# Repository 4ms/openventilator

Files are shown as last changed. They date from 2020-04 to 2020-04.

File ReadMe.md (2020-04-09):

# OpenVentilator

This project is a collaboration to update the OpenVentilator files provided by Medtronic to modern KiCad format as well as update BoM to currently available components.

If you'd like to contribute, please contact Seth (seth@kipro-pcb.com) for details.

## Getting Started

This includes links to useful resources and defines prerequisite programs or tools for contributing.

### SSH Keys

It is recommended to use a [SSH key](https://docs.gitlab.com/ee/gitlab-basics/create-your-ssh-keys.html) to pull/push.

For Windows users, [follow these instructions](https://docs.joyent.com/public-cloud/getting-started/ssh-keys/generating-an-ssh-key-manually/manually-generating-your-ssh-key-in-windows) to create an SSH key.

### Useful Resources

[Google Drive](https://drive.google.com/drive/folders/1fBbcaIb6aupdgDmfqB_Z8kfAjUOgFtCi) - Project specific Google drive.

[Medtronic Releases](https://www.medtronic.com/us-en/e/open-files/thank-you.html)

[GitLab basics guides](https://docs.gitlab.com/ee/gitlab-basics/)

[Gitflow](https://datasift.github.io/gitflow/IntroducingGitFlow.html)

### Tools

Install [Git](https://git-scm.com/) on your computer.

Either use KiCAD version 5.1.5 or the nightly builds.

[KiCAD v5.1.5](https://kicad-pcb.org/download/) - preferred

[KiCAD Nigthly Builds](https://launchpad.net/~js-reynaud/+archive/ubuntu/ppa-kicad)

**GerbView** - part of KiCAD.

File → Open Gerber Files. In “File Name” select *.phd for CR-5000 designs. Some of the polygons are not handled correctly in 5.1.5-3.

[PentaLogix ViewMate Free (Windows)](https://www.pentalogix.com/t/software-products/viewmate) 

You will need to create an account to download and get a serial number. Run File → Import → Gerber and then control-select all the .phd files for CR-5000 designs.

[GerberLogix](https://www.easylogix.de/products_detail.php?prog_id=1)

Works well with the free version for .phd files.  A little simpler than ViewMate

## Contributing

Please read [Contributing.md](Contributing.md) for information on cloning, branching, and sharing your work.

## Versioning

We should adhere to [SemVer](https://semver.org/) for our versioning process. Each PCB will have its own version number.

*Note that this is not completely settled.*

## Channels and Leads

If you are interested in working on a specific board, please head to the respective channels in the Slack organization. The leads for each board are provided below as well.

Be sure to check for pinned messages as well as the channel topic for more information as well.

### Hardware
**#battery-connection-board** for the Battery Connection Board. Lead by Valerie Hanson.

**#blower-driver-board** for the Blower Command Board. Lead by Gabe Soares.

**#buzzer-board** for the Buzzer Board RB0505. Lead by Yannick Liotta.

**#cpu-board** for the CPU Board. Lead by Seth Hillbrand.

**#mechanical-prototyping** for all mechanical components. Currently no lead.

**#power-management-board** for the Power Supply Board (Tantalum Less). Lead by Paul Petersen.

**#powerpack-board** for the Power Pack Board. Lead by George Ioakimedes.

**#turbine** for the blower turbine motor. Currently no lead.

### Firmware
**#firmware-pic** for questions relating to the PIC Firmware. Currently no lead.

**#firmware-st10** for questions relating to the ST Micro Firmware. Lead by Melvin Aguirre.

### Project Related
**#how-to-get-started** for help in setting up any part of the project. Lead by Adam Drewery.

**#general** for questions that you're unsure where they would belong.

**#openventilator** for high-level project discussions. For example, what version of KiCAD to use?

**#parts** for any questions related to parts. This can be creating them in KiCAD or sourcing them. For sourcing contact Ritika Sahai-Kar or Sophi Kravitz. For parts creation contact Adam Drewery.

## Parts

If creating new parts, follow the [KiCAD Library Convention](https://kicad-pcb.org/libraries/klc/).

Passives are an exception to this rule. Please create a library part per MPN.

### Symbol Parameters

The following fields are *required* for all parts.

**Reference**

**Value**

**Footprint**

**Documentation**

**Description**

**Item Number** - This is Medtronic's Item Number called out in their documentation.

**Manufacturer**

**Manufacturer_No**

### Pointing to the right libraries

Be sure you are not pointing to your own libraries. We want to work within the OpenVentilator project library.

Within a KiCAD project, click on Preferences -> Manage Symbol Libraries.

The Path to the libraries should contain **${KIPRJMOD}**.

*Note: The libraries are ultimately going to be brought into their own directory in the project. We will keep you posted with more information.*

## License

This project is licensed under the [Permissive License - Open Ventilator](Permissive License--Open Ventilator.pdf).

## Acknowledgements

Thanks to Marc Hillman for his contribution to the Battery Connection Board.

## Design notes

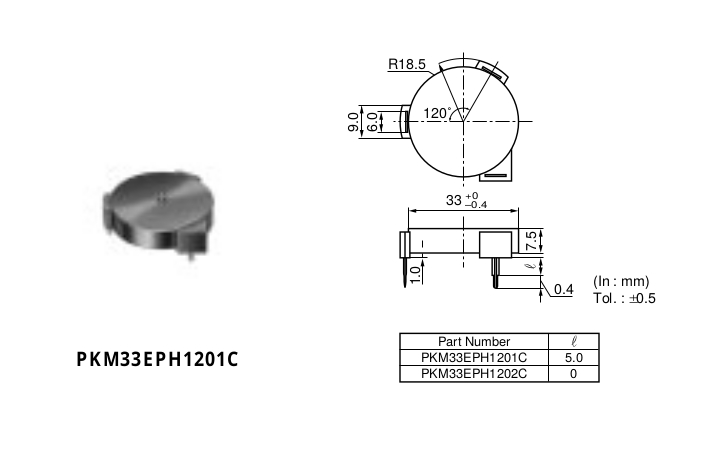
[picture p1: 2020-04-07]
GR106768 Buzzer/doc/PKM33EPH1201C.jpg

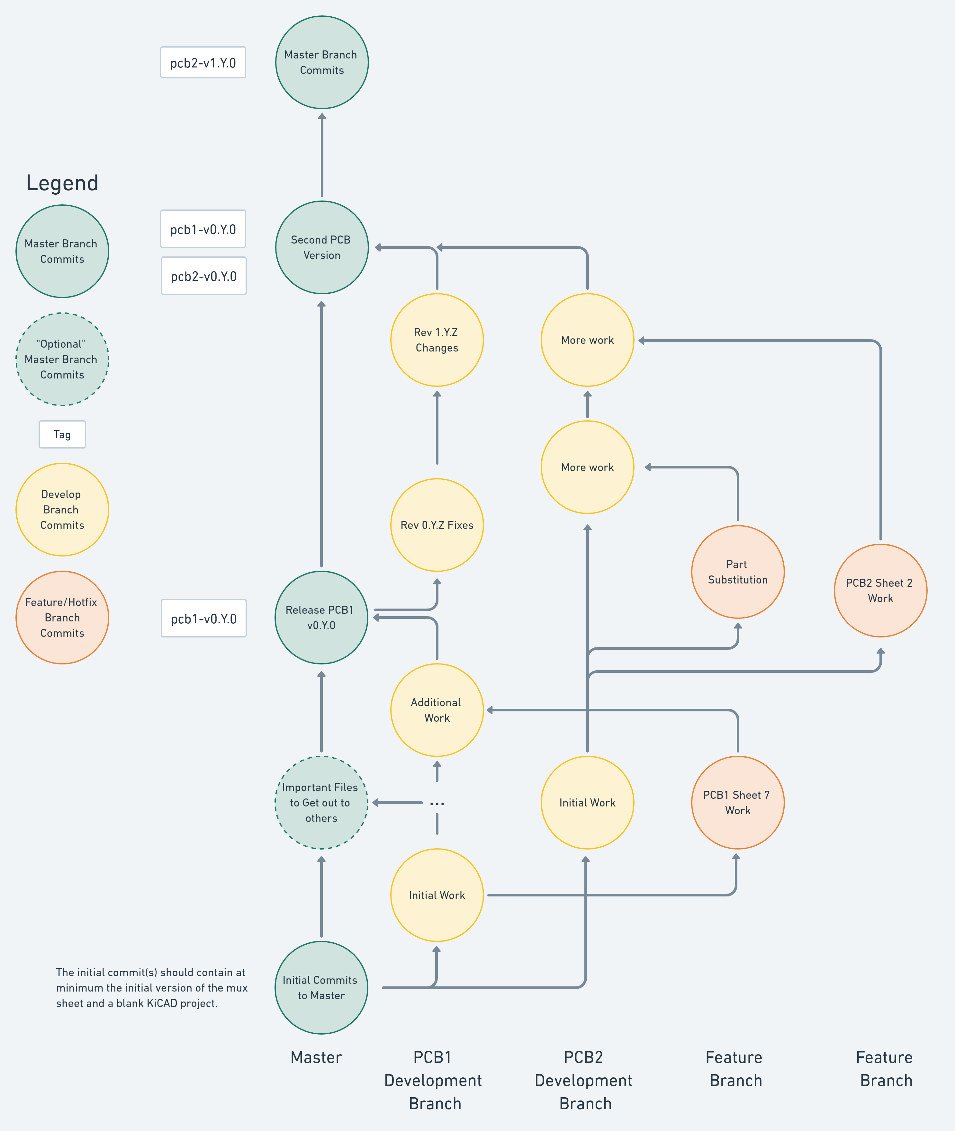
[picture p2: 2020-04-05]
git_version_control.png

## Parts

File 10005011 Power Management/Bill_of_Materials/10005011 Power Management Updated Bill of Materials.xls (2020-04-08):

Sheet: BoM Parts
Items in bold are left to do, awaiting info or just notes
Information current as of 4/7/2020
Item Description | Original Mfgr | Original Mfgr_PN | Qty | Ref Des | Mfgr | Mfgr_PN | Description | Source | Source_PN | Datasheet
POWER SUPPLY, 220VAC, 33VDC, 100W | XP POWER PLC | ECM100US33>2413 | 1 | ALIM1 | Note: Reached out to XP Power 4/3 inquiring about this part.
CAPACITOR,100NF,16V,+/-10%,X7R,0402 | MURATA | GRM155R71C104JA88J | 43 | C1,C3,C4,C5,C6,C8,C9,C12,C13,C15,C17,C25,C35,C36,C46,C58,C59,C63,C64,C69,C71,C75,C78,C82,C85,C86,C87,C88,C91,C92,C93,C96,C97,C101,C102,C103,C104,C105,C108,C122,C123,C124,C126 | Murata Electronics | GCM155R71C104KA55J | CAP CER 0.1UF 16V X7R 0402 | Digi-Key | 490-7998-1-ND | https://psearch.en.murata.com/capacitor/product/GCM155R71C104KA55%23.pdf
CAPACITOR CERAMIC, 10UF,+/-10%,50V | AVX | 22205C106K4Z4A | 19 | C10,C11,C14,C20,C26,C27,C28,C40,C41,C43,C51,C60,C66,C67,C73,C114,C136,C137,C138 | TDK Corporation | CGA9N3X7R1H106K230KB | CAP CER 10UF 50V X7R 2220 | Digi-Key | 445-7932-1-ND | https://product.tdk.com/info/en/catalog/datasheets/mlcc_automotive_general_en.pdf?ref_disty=digikey
CAPACITOR CERAMIC, 22UF,+/-10%,25V | KEMET_RMS1 | C2220X226K3RAC | 1 | C107 | KEMET | C2220X226K3RACAUTO | CAP CER 22UF 25V X7R 2220 | Digi-Key | 399-7061-1-ND | https://api.kemet.com/component-edge/download/specsheet/C2220X226K3RACAUTO.pdf
CAPACITOR,470PF,+/-10%,50V,0402 | VISHAY_RMS1 | VJ0402Y471KXAAC | 1 | C16 | Murata Electronics | GCM155R71H471KA37D | CAP CER 470PF 50V X7R 0402 | Digi-Key | 490-4913-1-ND | https://psearch.en.murata.com/capacitor/product/GCM155R71H471KA37%23.pdf
CAPACITOR CERAMIC,10NF,+/-10%,50V,0603 | YAGEO_RMS1 | 223858615636 | 15 | C18,C19,C22,C37,C47,C49,C52,C83,C99,C111,C115,C116,C117,C118,C119 | Yageo | CC0603KRX7R9BB103 | CAP CER 10000PF 50V X7R 0603 | Digi-Key | 311-1085-1-ND | https://www.yageo.com/upload/media/product/productsearch/datasheet/mlcc/UPY-GPHC_X7R_6.3V-to-50V_18.pdf
CAPACITOR CERAMIC, 10UF,+/-10%,16V | KEMET_RMS1 | C0805C106K4PAC | 2 | C2,C45 | KEMET | C0805C106K4PACTU | CAP CER 10UF 16V X5R 0805 | Digi-Key | 399-8012-1-ND | https://api.kemet.com/component-edge/download/datasheet/C0805C106K4PACTU.pdf
CAPACITOR CERAMIC, 4.7UF,+/-10%,50V | KEMET | C1210C475K5RACAUTO | 5 | C21,C29,C90,C134,C135 | KEMET | C1210C475K5RACAUTO | CAP CER 4.7UF 50V X7R 1210 | Digi-Key | 399-7049-1-ND | https://api.kemet.com/component-edge/download/specsheet/C1210C475K5RACAUTO.pdf
CAPACITOR CERAMIC, 100NF, +/-10%, 50V, X7R,0805 | YAGEO_RMS1 | 223858055649 | 15 | C23,C31,C55,C70,C79,C106,C109,C110,C112,C113,C131,C132,C133,C140,C141 | Yageo | CC0805KRX7R9BB104 | CAP CER 0.1UF 50V X7R 0805 | Digi-Key | 311-1140-1-ND | https://www.yageo.com/upload/media/product/productsearch/datasheet/mlcc/UPY-GPHC_X7R_6.3V-to-50V_18.pdf
CAPACITOR CERAMIC,4.7NF,+/-10%,50V,0603 | KEMET_RMS1 | C0603C472K5RACTU | 1 | C24 | KEMET | C0603C472K5RACTU | CAP CER 4700PF 50V X7R 0603 | Digi-Key | 399-1087-1-ND | https://api.kemet.com/component-edge/download/datasheet/C0603C472K5RACTU.pdf
CAPACITOR,4.7UF,+/-10%,16V, X5R, 0805 | AVX_RMS1 | 0805YD475KAT2A | 2 | C30,C80 | AVX Corporation | 0805YD475KAT2A | CAP CER 4.7UF 16V X5R 0805 | Digi-Key | 478-5166-1-ND | http://datasheets.avx.com/cx5r.pdf
CAPACITOR, 1UF, +/-10%, 16V, 0805 | AVX_RMS1 | 0805YC105KAT2A | 2 | C32,C57 | AVX Corporation | 0805YC105KAT2A | CAP CER 1UF 16V X7R 0805 | Digi-Key | 478-5034-1-ND | http://datasheets.avx.com/X7RDielectric.pdf
CAPACITOR,2.2UF,+/-10%,16V,1206 | MURATA MANUFACTURING CO., LTD. | GCM31MR71E225KA57L | 1 | C33 | Taiyo Yuden | EMK316B7225KLHT | CAP CER 2.2UF 16V X7R 1206 | Digi-Key | 587-3329-1-ND | https://ds.yuden.co.jp/TYCOMPAS/ut/detail?pn=EMK316B7225KLHT%20%20&u=M
CAPACITOR CERAMIC, 22UF,+/-10%,16V | JOHANSON DIELECTRICS_RMS1 | 160S41X226KV4E | 2 | C34,C65 | Taiyo Yuden | EMK325BJ226KMHP | CAP CER 22UF 16V X5R 1210 | Digi-Key | 587-5432-1-ND | https://ds.yuden.co.jp/TYCOMPAS/ut/detail?pn=EMK325BJ226KMHP%20&u=M
CAPACITOR,220NF,+/-20%,16V,0603 | VISHAY_RMS1 | VJ0603V224MXJCW1BC | 2 | C38,C39 | TDK Corporation | CGA3E2X7R1C224M080AA | CAP CER 0.22UF 16V X7R 0603 | Digi-Key | 445-12535-1-ND | https://product.tdk.com/info/en/catalog/datasheets/mlcc_automotive_general_en.pdf?ref_disty=digikey
CAPACITOR ELECTROLYTIC, 330UF,35V | PANASONIC_RMS1 | EEEFK1V331P | 2 | C42,C125 | Panasonic Electronic Components | EEE-FK1V331P | CAP ALUM 330UF 20% 35V SMD | Digi-Key | PCE3841CT-ND | http://industrial.panasonic.com/www-cgi/jvcr13pz.cgi?E+PZ+3+ABA0120+EEEFK1V331P+7+WW
CAPACITOR ELECTROLYTIC, 220UF,16V+/-20% | PANASONIC_RMS1 | EEEFK1C221P | 1 | C44 | Panasonic Electronic Components | EEE-FK1C221P | CAP ALUM 220UF 20% 16V SMD | Digi-Key | PCE3787CT-ND | http://industrial.panasonic.com/www-cgi/jvcr13pz.cgi?E+PZ+3+ABA0120+EEEFK1C221P+7+WW
CAPACITOR,47 PF,+/-5%,50V,0402 | MURATA MANUFACTURING CO., LTD. | GRM1555C1H470JA01D | 7 | C48,C120,C121,C127,C128,C129,C130 | Murata Electronics | GCM1555C1H470JA16D | CAP CER 47PF 50V C0G/NP0 0402 | Digi-Key | 490-10670-1-ND | https://www.murata.com/~/media/webrenewal/support/library/catalog/products/capacitor/mlcc/c03e.ashx?la=en-us
CAPACITOR,220NF,+/-10%,16V,X7R,1206 | VISHAY_RMS1 | VJ1206Y224JXAAT | 1 | C50 | KEMET | C1206C224J5RACTU | CAP CER 0.22UF 50V X7R 1206 | Digi-Key | 399-1252-1-ND | https://api.kemet.com/component-edge/download/datasheet/C1206C224J5RACTU.pdf
CAPACITOR ARRAY, 47PF, 50V, +/-10%,NPO,0612 | YAGEO_RMS1 | 225514611532 | 5 | C53,C61,C62,C98,C100 | KEMET | CA064C470K5GAC7800 | CAP ARRAY 47PF 50V NP0 0612 | Digi-Key | 399-10028-1-ND | https://media.digikey.com/pdf/Data%20Sheets/Kemet%20PDFs/COG_Dielectric_Rev_Mar_2015.pdf
CAPACITOR ELECTROLYTIC, 100UF,35V,+/-10% | PANASONIC_RMS1 | EEEFK1V101P | 1 | C54 | Panasonic Electronic Components | EEE-FK1V101P | CAP ALUM 100UF 20% 35V SMD | Digi-Key | PCE3835CT-ND | http://industrial.panasonic.com/www-cgi/jvcr13pz.cgi?E+PZ+3+ABA0120+EEEFK1V101P+7+WW
CAPACITOR,56PF,50V,+/-5%,0603,NPO | YAGEO_RMS1 | 223886715569 | 1 | C68 | Yageo | CC0603JRNPO9BN560 | CAP CER 56PF 50V C0G/NPO 0603 | Digi-Key | 311-1066-1-ND | https://www.yageo.com/upload/media/product/productsearch/datasheet/mlcc/UPY-GP_NP0_16V-to-50V_18.pdf
CAPACITOR, 33PF, +/-5%,50V,NPO, 0603 | MURATA MANUFACTURING CO., LTD. | GRM1885C1H330JA01D | 1 | C7 | Samsung Electro-Mechanics | CL10C330JB81PNC | CAP CER 33PF 50V C0G/NP0 0603 | Digi-Key | 1276-2264-1-ND | http://www.samsungsem.com/kr/support/product-search/mlcc/CL10C330JB81PNC.jsp
CAPACITOR,33NF,+/-10%,16V,X7R,0603 | AVX_RMS1 | 0603YC333KAT2A | 1 | C72 | AVX Corporation | 0603YC333KAT2A | CAP CER 0.033UF 16V X7R 0603 | Digi-Key | 478-5898-1-ND | http://datasheets.avx.com/X7RDielectric.pdf
CAPACITOR,1NF,+/-10%,50V,X7R,0603 | AVX_RMS1 | 06035C102KAT2A | 1 | C74 | AVX Corporation | 06035C102KAT2A | CAP CER 1000PF 50V X7R 0603 | Digi-Key | 478-1215-1-ND | http://datasheets.avx.com/X7RDielectric.pdf
CAPACITOR,330NF,+/-10%,16V,0805,X7R | YAGEO_RMS1 | 222278015556 | 1 | C76 | Yageo | CC0805JKX7R7BB334 | CAP CER 0.33UF 16V X7R 0805 | Digi-Key | 311-4215-1-ND | https://www.yageo.com/upload/media/product/productsearch/datasheet/mlcc/UPY-GPHC_X7R_6.3V-to-50V_18.pdf
CAPACITOR,100PF,50V,+/-5%,C0G,0402 | MURATA MANUFACTURING CO., LTD. | GRM1555C1H101JD01D | 2 | C77,C81 | Samsung Electro-Mechanics | CL10C101JB81PNC | CAP CER 100PF 50V C0G/NP0 0603 | Digi-Key | 1276-2162-1-ND | http://www.samsungsem.com/kr/support/product-search/mlcc/CL10C101JB81PNC.jsp
CAPACITOR,1UF,+/-10%,6.3V,X5R,0603 | MURATA MANUFACTURING CO., LTD. | GRM188B11A105KA61D | 1 | C84 | KEMET | C0603C105K9PACTU | CAP CER 1UF 6.3V X5R 0603 | Digi-Key | 399-7848-1-ND | https://api.kemet.com/component-edge/download/datasheet/C0603C105K9PACTU.pdf
CAPACITOR CERAMIC, 100UF,+/-20%,6.3V | KEMET_RMS1 | C1206C107M9PAC | 1 | C89 | KEMET | C1206C107M9PACTU | CAP CER 100UF 6.3V X5R 1206 | Digi-Key | 399-5620-1-ND | https://api.kemet.com/component-edge/download/specsheet/C1206C107M9PACTU.pdf
CAPACITOR CERAMIC,22PF,+/-5%,50V,0603 | SAMSUNG_RMS1 | CL10C220JB8NNNC | 2 | C94,C95 | Samsung Electro-Mechanics | CL10C220JB8NNNC | CAP CER 22PF 50V C0G/NP0 0603 | Digi-Key | 1276-1023-1-ND | http://www.samsungsem.com/kr/support/product-search/mlcc/CL10C220JB8NNNC.jsp
DIODE SCHOTTKY, 40V, 1A | NXP SEMICONDUCTORS_RMS1 | PRLL5819,115 | 3 | CR1,CR2,D19 | Diodes Incorporated | 1N5819HW-7-F | DIODE SCHOTTKY 40V 1A SOD123 | Digi-Key | 1N5819HW-FDICT-ND | https://www.diodes.com/assets/Datasheets/ds30217.pdf
THERMISTOR, 10K OHM, B4300. +/-5% | EPCOS_RMS1 | B57164K103J | 1 | CT1 | Panasonic Electronic Components | ERT-J1VR103J | THERMISTOR NTC 10KOHM 4250K 0603 | Digi-Key | P10547CT-ND | http://industrial.panasonic.com/www-cgi/jvcr13pz.cgi?E+PZ+3+AUA0001+ERTJ1VR103J+7+WW
DIODE SCHOTTKY, 30V, 200MA | NXP SEMICONDUCTORS_RMS1 | BAT54,215 | 4 | D1,D17,D18,D20 | ON Semiconductor | BAT54LT1G | DIODE SCHOTTKY 30V 200MA SOT23-3 | Digi-Key | BAT54LT1GOSTR-ND | http://www.onsemi.com/pub/Collateral/BAT54LT1-D.PDF
DIODE ZENER, 0.35,5.1V, SOT23 | NXP SEMICONDUCTORS_RMS1 | BZX84-C5V1 | 2 | D10,D12 | Diodes Incorporated | BZX84C5V1-7-F | DIODE ZENER 5.1V 300MW SOT23-3 | Digi-Key | BZX84C5V1-FDITR-ND | https://www.diodes.com/assets/Datasheets/ds18001.pdf
DIODE, 33V, VCL 53.3V, 1500W | FAIRCHILD SEMICONDUCTOR CORPORATION | SMCJ33CA | 1 | D13 | Diodes Incorporated | SMCJ33CAQ-13-F | TRANSIENT VOLTAGE SUPPRESSOR,SMC | Digi-Key | SMCJ33CAQ-13-FDICT-ND | https://www.diodes.com/assets/Datasheets/ds40741.pdf
DIODE SCHOTTKY DOUBLE,30V, 200MA,SOT23 | NXP SEMICONDUCTORS_RMS1 | BAT54C,215 | 5 | D2,D7,D14,D15,D16 | ON Semiconductor | BAT54C | DIODE ARRAY SCHOTTKY 30V SOT23-3 | Digi-Key | BAT54CFSCT-ND | https://media.digikey.com/pdf/Data%20Sheets/ON%20Semiconductor%20PDFs/BAT54(A,C,S).pdf
DIODE TRANSIENT 600W,36V | LITTLEFUSE | SZ1SMB36AT3G | 2 | D3,D21 | Littelfuse Inc. | SZ1SMB36AT3G | TVS DIODE 36V 58.1V SMB | Digi-Key | F11561CT-ND | https://www.littelfuse.com/~/media/electronics/datasheets/tvs_diodes/littelfuse_tvs_diode_sz1smb_datasheet.pdf.pdf
DIODE ZENER, 0.35W,4.7V | NXP SEMICONDUCTORS_RMS1 | BZX84-C4V7 | 1 | D4 | Rochester Electronics, LLC | BZX84C4V7 | DIODE ZENER, 0.35W,4.7V | Digi-Key | 2156-BZX84C4V7-ONTR-ND | https://4donline.ihs.com/images/VipMasterIC/IC/ONSM/ONSM-S-A0003405162/ONSM-S-A0003405162-1.pdf?hkey=EC6BD57738AE6E33B588C5F9AD3CEFA7
DIODE SCHOTTKY, 3A, 40V | STMICROELECTRONICS | STPS340U | 3 | D5,D6,D11 | STMicroelectronics | STPS340U | DIODE SCHOTTKY 40V 3A SMB | Digi-Key | 497-2465-1-ND | http://www.st.com/content/ccc/resource/technical/document/datasheet/bb/db/21/0c/04/d9/41/a5/CD00000844.pdf/files/CD00000844.pdf/jcr:content/translations/en.CD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
DIODE SCHOTTKY, 40V, 500MA | PHILIPS | PMEG4005ET | 2 | D8,D9 | Nexperia USA Inc. | PMEG4005ET,215 | DIODE SCHOTTKY 40V 500MA SOT23 | Digi-Key | 1727-3878-1-ND | https://assets.nexperia.com/documents/data-sheet/PMEGXX05ET_SER.pdf
FUSE HOLDER 5X20 | SCHURTER | 31.8225 | 1 | F1 | Schurter Inc. | 31.8225 | FUSE BLOK CARTRIDGE 500V 10A SMD | Digi-Key | 486-1723-1-ND | http://www.schurterinc.com/bundles/snceschurter/epim/_ProdPool_/newDS/en/typ_OGN-SMD.pdf
FILTER CC, 1MHZ-1GHZ, 10A, 50V | MURATA MANUFACTURING CO., LTD. | BNX002-01 | 3 | FLTR1,FLTR2,FLTR3 | Murata Electronics | BNX002-11 | EMI Filter Circuits 12.5mm 50V 10A 100Mohm EMI Filter | Mouser | 81-BNX002-11 | https://www.mouser.com/datasheet/2/281/BNX002-11-1569986.pdf
DUAL DIFFERENTIAL COMPARATOR, SOIC8 | TEXAS INSTRUMENTS_RMS1 | LM393D | 1 | IC1 | ON Semiconductor | LM393DR2G | IC COMP DUAL OFFSET LV 8SOIC | Digi-Key | LM393DR2GOSCT-ND | http://www.onsemi.com/pub/Collateral/LM393-D.PDF
IC,SYNCHRONOUS CONTROLLER,SSOP | LINEAR TECHNOLOGY_RMS1 | LTC3780IG#TRPBF | 1 | IC10 | Analog Devices / Linear Technology | LTC3780IG#PBF | Switching Voltage Regulators High Power Buck-Boost DC/DC Controller | Mouser | 584-LTC3780IG#PBF | https://www.mouser.com/datasheet/2/609/LTC3780-1541987.pdf
REGULATOR, 5.5V TO 36V,3A | TEXAS INSTRUMENTS_RMS1 | TPS 5430 DDA | 1 | IC11 | Texas Instruments | TPS5430DDARG4 | IC REG BUCK ADJUSTABLE 3A 8SOPWR | Digi-Key | 296-35990-1-ND | https://www.ti.com/lit/ds/symlink/tps5431.pdf
IC,VOLTAGE REFERENCE,5MA,3V +/-2%,SOT23 | NATIONAL SEMICONDUCTOR_RMS1 | LM4120AIM5-3.0/NOPB | 1 | IC12 | Texas Instruments | LM4120AIM5-3.0/NOPB | IC VREF SERIES 0.2% SOT23-5 | Digi-Key | LM4120AIM5-3.0/NOPBCT-ND | http://www.ti.com/general/docs/suppproductinfo.tsp?distId=10
IC,SWITCHING REGULATOR,SSOP | LINEAR TECHNOLOGY_RMS1 | LTC1435IG#TRPBF | 1 | IC13 | Linear Technology/Analog Devices | LTC1435CS#PBF | IC REG CTRLR BUCK 16SOIC | Digi-Key | LTC1435CS#PBF-ND | http://www.linear.com/docs/2213
IC,MICROCONTROLLER,TQFP100 | CYPRESS SEMICONDUCTOR CORPORATION | CY7C67300-100AXI | 1 | IC15 | Rochester Electronics, LLC | CY7C67300-100AXE | USB BUS CONTROLLER | Digi-Key | 2156-CY7C67300-100AXE-CY-ND | https://4donline.ihs.com/images/VipMasterIC/IC/CYPR/CYPRS08906/CYPRS08906-1.pdf?hkey=EC6BD57738AE6E33B588C5F9AD3CEFA7
IC,RAM,3V3,64KX16,10NS,TSOP | CYPRESS SEMICONDUCTOR CORPORATION | CY7C1021DV33-10ZSXI | 1 | IC16 | Cypress Semiconductor Corp | CY7C1021CV33-10ZSXA | IC SRAM 1M PARALLEL 44TSOP II | Digi-Key | 428-3269-ND | https://www.cypress.com/file/38801/download
IC,EEPROM,2.5V-5.5V,12C SERIES, 64KBYTES, SOIC8 | MICROCHIP TECHNOLOGY_RMS1 | 24LC512-I/SM | 1 | IC17 | Microchip Technology | 24LC512-I/SN | IC EEPROM 512K I2C 400KHZ 8SOIC | Digi-Key | 24LC512-I/SN-ND | http://www.microchip.com/mymicrochip/filehandler.aspx?ddocname=en546203
IC,NON INVERTING BUS TRANSCEIVER,MSOP | TEXAS INSTRUMENTS_RMS1 | SN74LVC2T45DCTR | 3 | IC18,IC19,IC20 | Texas Instruments | SN74LVC2T45DCTR | IC TRNSLTR BIDIRECTIONAL SM8 | Digi-Key | 296-16845-1-ND | http://www.ti.com/general/docs/suppproductinfo.tsp?distId=10
SINGLE 2 INPUT POSITIVE AND GATE, SOT23 | TEXAS INSTRUMENTS_RMS1 | SN74AHC1G08DBVR | 1 | IC2 | Texas Instruments | SN74AHC1G08DBVR | IC GATE AND 1CH 2-INP SOT23-5 | Digi-Key | 296-1091-1-ND | http://www.ti.com/general/docs/suppproductinfo.tsp?distId=10
IC,RAIL TO RAIL COMPARATOR, 44V, SOT23 | LINEAR TECHNOLOGY_RMS1 | LT1716IS5#TRPBF | 2 | IC21,IC22 | Linear Technology/Analog Devices | LT1716IS5#TRPBF | IC COMP OTT R-R 44V TSOT-23-5 | Digi-Key | LT1716IS5#TRPBFCT-ND | http://www.linear.com/docs/3319
IC,VOLTAGE REFERENCE,SHUNT, 5V,SOT23 | NATIONAL SEMICONDUCTOR_RMS1 | LM4040DIM3-5.0 | 2 | IC23,IC24 | Texas Instruments | LM4040DIM3-5.0/NOPB | IC VREF SHUNT 1% SOT23-3 | Digi-Key | LM4040DIM3-5.0NS/NOPBCT-ND | http://www.ti.com/general/docs/suppproductinfo.tsp?distId=10
IC,REGULATOR, 24V +/-4%, 500MA, DPACK | ST MICROELECTRONIC | L78M24CDT-TR | 1 | IC25 | STMicroelectronics | L78M24CDT-TR | IC REG LINEAR 24V 500MA DPAK | Digi-Key | 497-1213-1-ND | http://www.st.com/content/ccc/resource/technical/document/datasheet/d7/5f/dc/5c/d5/b6/48/7c/CD00000447.pdf/files/CD00000447.pdf/jcr:content/translations/en.CD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
IC,BUS SWITCH,SC70 | FAIRCHILD SEMICONDUCTOR_RMS1 | NC7SZ66P5X | 2 | IC26,IC27 | ON Semiconductor | NC7SZ66P5X | IC BUS SWITCH SPST SGL LV SC70-5 | Digi-Key | NC7SZ66P5XCT-ND | https://www.onsemi.cn/PowerSolutions/document/NC7SZ66-D.pdf
IC,VOLTAGE REGULATOR,5V +/-4%,500MA, DPACK | ST MICROELECTRONIC | L78M05CDT-TR | 1 | IC28 | STMicroelectronics | L78M05CDT-TR | IC REG LINEAR 5V 500MA DPAK | Digi-Key | 497-1203-1-ND | http://www.st.com/content/ccc/resource/technical/document/datasheet/d7/5f/dc/5c/d5/b6/48/7c/CD00000447.pdf/files/CD00000447.pdf/jcr:content/translations/en.CD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
MICROCON,8 BIT, FLASH 64K,RAM3966 BYTES,TQFP64 | MICROCHIP TECHNOLOGY_RMS1 | PIC18F6622-I/PT | 1 | IC3 | Microchip Technology | PIC18F6622-I/PT | IC MCU 8BIT 64KB FLASH 64TQFP | Digi-Key | PIC18F6622-I/PT-ND | http://www.microchip.com/mymicrochip/filehandler.aspx?ddocname=en021341
USB/UART, LQFP | FTDI_RMS1 | FT2232D | 1 | IC4 | FTDI, Future Technology Devices International Ltd | FT2232D-REEL | IC USB FS DUAL UART/FIFO 48-LQFP | Digi-Key | 768-1010-1-ND | http://www.ftdichip.com/Support/Documents/DataSheets/ICs/DS_FT2232D.pdf
IC, SERIAL TO 1-WIRE DRIVER, SOIC8 | MAXIM_RMS1 | DS2480B+T&R | 1 | IC5 | Rochester Electronics, LLC | DS2480B | DS2480 SERIAL 1-WIRE LINE DRIVER | Digi-Key | 2156-DS2480B-MA-ND | https://4donline.ihs.com/images/VipMasterIC/IC/MAXM/MAXM-S-A0000633411/MAXM-S-A0000663982-1.pdf?hkey=EC6BD57738AE6E33B588C5F9AD3CEFA7
IC, COMPARATOR, SOT23-6 | TEXAS INSTRUMENTS_RMS1 | TLV3012AIDBVR | 1 | IC6 | Texas Instruments | TLV3012AIDBVR | IC COMPARATOR 1.8V W/REF SOT23-6 | Digi-Key | 296-39261-1-ND | http://www.ti.com/general/docs/suppproductinfo.tsp?distId=10
IC,CURRENT SHUNT MONITOR,MSOP | TEXAS INSTRUMENTS_RMS1 | INA170EA | 1 | IC7 | Texas Instruments | INA170EA/250 | IC CURRENT SHUNT MONITOR 8VSSOP 0.5% | Digi-Key | 296-28958-1-ND | http://www.ti.com/general/docs/suppproductinfo.tsp?distId=10
REGULATOR 3.3 V 2% 500MA LOW DROPOUT,DPACK | ST MICROELECTRONIC | LF33CDT | 1 | IC8 | STMicroelectronics | LF33CDT-TR | IC REG LINEAR 3.3V 500MA DPAK | Digi-Key | 497-1532-1-ND | http://www.st.com/content/ccc/resource/technical/document/datasheet/c4/0e/7e/2a/be/bc/4c/bd/CD00000546.pdf/files/CD00000546.pdf/jcr:content/translations/en.CD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
IC,CURRENT AMPLIFIER,MSOP | LINEAR TECHNOLOGY_RMS1 | LT1620CMS8 | 2 | IC9,IC14 | Linear Technology/Analog Devices | LT1620CMS8#PBF | IC CURR SENSE 1 CIRCUIT 8MSOP | Digi-Key | LT1620CMS8#PBF-ND | http://www.linear.com/docs/2317
USB MINI B | MOLEX_RMS1 | 54819-0519 | 1 | J1 | Molex | 54819-0519 | USB Connectors USB Mini-B Recept On-The-Go Rt.Angle | Mouser | 538-54819-0519 | https://www.mouser.com/datasheet/2/276/0548190519_IO_CONNECTORS-228766.pdf
CONNECTOR FEMALE,2.54MM SPACING,8.5MM +/-0.15 | HARWIN (012775) | M20-7830546 | 1 | J10 | Harwin Inc. | M20-7830546 | CONN RCPT 10POS 0.1 TIN PCB | Digi-Key | 952-1797-ND | https://cdn.harwin.com/pdfs/M20-783.pdf
CONNECTOR USB A | MOLEX_RMS1 | 67329-8001 | 2 | J12,J13 | Molex | 673298001 | CONN RCPT USB2.0 TYPEA 4POS R/A | Digi-Key | WM17151-ND | https://www.molex.com/pdm_docs/sd/673298001_sd.pdf
ZH RIGHT CONNECTOR PINS 4 / 1.5 MM 1A/50V | J.S.T. CORPORATION | B4B-ZR-SM4-TF (LF)(SN) | 1 | J14 | JST Sales America Inc. | B4B-ZR-SM4-TFT(LF)(SN) | CONN HEADER SMD 4POS 1.5MM | Digi-Key | 455-3273-1-ND | http://www.jst-mfg.com/product/pdf/eng/eZH.pdf
CONNECTOR, ZH RIGHT, PINS 6 / 1.5 MM 1A/50V | J.S.T. CORPORATION | B6B-ZR-SM4-TF (LF)(SN) | 1 | J2 | JST Sales America Inc. | B6B-ZR-SM4-TF(LF)(SN) | CONN HEADER SMD 6POS 1.5MM | Digi-Key | 455-1685-1-ND | http://www.jst-mfg.com/product/pdf/eng/eZH.pdf
CONNECTOR KK PC BOARD 12 CIRCUITS, 3.96MM,5A,250V | MOLEX_RMS1 | 26-11-2123 | 1 | J3 | Molex | 9484128 | CONN RCPT 12POS 0.156 TIN PCB | Digi-Key | WM13509-ND | https://www.molex.com/pdm_docs/sd/009481124_sd.pdf
CONNECTOR KK PC BOARD, 3 CIRCUITS, 3.96MM, 5A, 250V | MOLEX_RMS1 | 26-11-2033 | 1 | J4 | Molex | 9484038 | CONN RCPT 3POS 0.156 TIN PCB | Digi-Key | WM13500-ND | https://www.molex.com/pdm_docs/sd/009481034_sd.pdf
IC SOCKET CONNECTOR SIZE 1, 6 CIRCUITS, 4.5 A | ODU_RMS1 | GF1LON-P06QF00-0000 | 1 | J5 | ODU | GF1L0C-P06QF00-0000 |  |  |  | https://connector.odu.de/pdf-controller.html | This is the DC power jack. HW spec says 10.8 to 33V, 3A max.
CONNECTOR HEADER, 2 CIRCUITS, 2.54MM, 4A, 250V | MOLEX_RMS1 | 22-27-2021 | 1 | J6 | Molex | 22272021 | CONN HEADER VERT 2POS 2.54MM | Digi-Key | WM4111-ND | https://www.molex.com/pdm_docs/sd/022272021_sd.pdf
HEADER CONNECTOR, VERTICAL, 26 PINS | FCI/BERG | 75869-105LF | 1 | J7 | Amphenol ICC (FCI) | 75869-105LF | CONN HEADER VERT 26POS 2.54MM | Digi-Key | 609-1777-ND | https://cdn.amphenol-icc.com/media/wysiwyg/files/drawing/75869.pdf
CONNECTOR MICRO-FIT, 2 CIRCUITS,3MM,5A,250V | MOLEX_RMS1 | 43650-0224 | 1 | J9 | Molex | 436500224 | CONN HEADER SMD 2POS 3MM | Digi-Key | WM2627CT-ND | https://www.molex.com/pdm_docs/sd/436500224_sd.pdf
FERRITE, SMD, 220OHM | MURATA_RMS1 | BLM21PG221SH1D | 6 | L1,L7,L10,L24,L25,L26 | Bourns Inc. | MH2029-221Y | FERRITE BEAD 220 OHM 0805 1LN | Digi-Key | MH2029-221YTR-ND | https://www.bourns.com/docs/Product-Datasheets/mh.pdf
INDUCTOR, 47UH +/-20%,3.8A,WE-PD-XXL | WURTH ELEKTRONIK GMBH | 7447709470 | 1 | L12 | Würth Elektronik | 7447709470 | FIXED IND 47UH 3.8A 60 MOHM SMD | Digi-Key | 732-1246-1-ND | https://katalog.we-online.de/pbs/datasheet/7447709470.pdf
INDUCTOR,470NH,450MA +/-20%,C1206 | WURTH ELEKTRONIK GMBH | 744764004 | 2 | L13,L14 | Würth Elektronik | 744764004 | Fixed Inductors WE-GF SMT Wire Wound Inductor | Mouser | 710-744764004 | https://www.mouser.com/datasheet/2/445/744764004-1710660.pdf
INDUCTOR,33UH +/-10% | WURTH ELEKTRONIK GMBH | 74456133 | 1 | L2 | Würth Elektronik | 74456133 | FIXED IND 33UH 2.3A 120 MOHM SMD | Digi-Key | 732-1353-1-ND | https://katalog.we-online.de/pbs/datasheet/74456133.pdf
INDUCTOR, POWER CHOKE, 47UH, 8A | WURTH ELEKTRONIK GMBH | P01/00004 | 1 | L3 | Bourns Inc. | 2209-V-RC | FIXED IND 47UH 6.7A 24 MOHM TH | Digi-Key | M8871-ND | https://www.bourns.com/docs/Product-Datasheets/2200_series.pdf | Switching regulator inductor in the 24V source. HW spec says 4A current limited. This cross will fit and should work but is not exact
INDUCTOR, MINIATURE, 220UH, 220MA,WE-TPC | WURTH ELEKTRONIK GMBH | 74455222 | 1 | L4 | Würth Elektronik | 74455222 | WE-PD4 SMT POWER INDUCTOR SIZE T | Digi-Key | 732-14074-1-ND | https://katalog.we-online.com/pbs/datasheet/74455222.pdf
SMD FERRITE, 1A,1206 | WURTH ELEKTRONIK GMBH | 74279218 | 2 | L5,L61 | Würth Elektronik | 74279218 | FERRITE BEAD 600 OHM 1206 1LN | Digi-Key | 732-1623-1-ND | https://katalog.we-online.de/pbs/datasheet/74279218.pdf
SMD FERRITE 200MA | WURTH ELEKTRONIK GMBH | 74279266 | 18 | L6,L15,L16,L17,L18,L19,L20,L21,L22,L23,L43,L44,L45,L46,L47,L48,L49,L50 | Würth Elektronik | 74279266 | FERRITE BEAD 1 KOHM 0603 1LN | Digi-Key | 732-4484-1-ND | https://katalog.we-online.de/pbs/datasheet/74279266.pdf
COMMON MODE CHOKE COIL 550OHM | MURATA_RMS1 | DLP31SN551ML2L | 3 | L8,L9,L11 | Murata Electronics | DLP31SN551ML2L | CMC 100MA 2LN 550 OHM SMD | Digi-Key | 490-4021-1-ND | https://www.murata.com/en-eu/products/productdata/8796756410398/EFLE0007.pdf
SMD VARISTOR, 5.5V,C0603 | EPCOS_RMS1 | B72500T0040M060 | 5 | ML1,ML2,ML3,ML6,ML8 | TDK Electronics Inc. | B72500T0040M060 | VARISTOR 8V 30A 0603 | Digi-Key | 495-2595-1-ND | https://www.tdk-electronics.tdk.com/inf/75/db/CTVS_14/Standard_series.pdf
VARISTOR, CMS PROTECTION, 30VRMS, 38 VDC, 1206, | EPCOS_RMS1 | B72520T0300K062 | 1 | ML4 | TDK Electronics Inc. | B72520T0300K062 | VARISTOR 47V 200A 1206 | Digi-Key | 495-2602-1-ND | https://www.tdk-electronics.tdk.com/inf/75/db/CTVS_14/Standard_series.pdf
RESETTABLE FUSE, 1.1A,C1812 | BOURNS_RMS1 | MF-MSMF-110-2 | 1 | PCT1 | Bourns Inc. | MF-MSMF110/16-2 | PTC RESET FUSE 16V 1.1A 1812 | Digi-Key | MF-MSMF110/16-2CT-ND | https://www.bourns.com/docs/Product-Datasheets/mfmsmf.pdf
VARISTOR, CMS PROTECTION ESD SURGE SUPPRESSOR,C0603 | WURTH ELEKTRONIK GMBH | 82356050050 | 6 | PG1,PG2,PG3,PG4,PG5,PG6 | Würth Elektronik | 82356050050 | ESD SUPPRESSOR 0603; 5VDC; 5PF | Digi-Key | 732-13295-1-ND | https://katalog.we-online.de/pbs/datasheet/82356050050.pdf
TEST POINT | NICOMATIC_RMS1 | C12000B | 1 | PT1 | Note: Have not found in distribution but available from Nicomatic directly
IC,RESONATOR, 6MHZ +/-0.5%,CMS | MURATA MANUFACTURING CO., LTD. | CSTCR6M00G53-R0 | 1 | Q1 | Murata Electronics | CSTCR6M00G53-R0 | Resonators 6.00MHz 0.5% | Mouser | 81-CSTCR6M00G53 | https://www.mouser.com/datasheet/2/281/p16e-522700.pdf
CRYSTAL,QUARTZ, 12MHZ | CHUNGHO ELCOM | MSM120FRA | 1 | Q3 | ECS Inc. | ECS-120-20-5PX-TR | CRYSTAL 12.000 MHZ 20PF SMD | Digi-Key | XC2080CT-ND | https://www.ecsxtal.com/store/pdf/csm-7x.pdf | Per Cypress datasheet: crystal to be parallel resonant, fundamental 500uW, 20-33pf, +/- 500ppm freq. stability, +/- 5% 12MHz. Per gerbers, looks like HC49 can
RESISTOR, 27K OHM, 0.063W, +/-0.1%,0603 | SUSUMU CO. | RG1608P-273-B-T5 | 2 | R1,R124 | Susumu | RG1608P-273-B-T5 | RES SMD 27K OHM 0.1% 1/10W 0603 | Digi-Key | RG16P27.0KBCT-ND | https://media.digikey.com/pdf/Data%20Sheets/Susumu%20PDFs/RG_RM_RGH_Oct2012.pdf
RESISTOR,10K OHM.0.063W,+/-1%,0603 | YAGEO_RMS1 | RC0603FR-0710KL | 32 | R10,R12,R16,R21,R23,R24,R25,R27,R28,R29,R30,R34,R36,R37,R38,R39,R40,R41,R46,R49,R50,R51,R60,R68,R77,R83,R84,R86,R89,R98,R105,R106 | Yageo | RC0603FR-0710KL | RES SMD 10K OHM 1% 1/10W 0603 | Digi-Key | 311-10.0KHRCT-ND | https://www.yageo.com/upload/media/product/productsearch/datasheet/rchip/PYu-RC_Group_51_RoHS_L_10.pdf
RESISTOR,2.7K OHM,0.063W,+/-1%,0603 | BOURNS_RMS1 | CR0603-FX-272ELF | 1 | R103 | Panasonic Electronic Components | ERJ-3EKF2701V | RES SMD 2.7K OHM 1% 1/10W 0603 | Digi-Key | P2.70KHCT-ND | https://industrial.panasonic.com/cdbs/www-data/pdf/RDA0000/AOA0000C304.pdf
RESISTOR,1M OHM,0.063W,+/-1%,0603 | YAGEO_RMS1 | 232270461005L | 3 | R104,R110,R113 | Yageo | RC0603FR-071ML | RES SMD 1M OHM 1% 1/10W 0603 | Digi-Key | 311-1.00MHRTR-ND | https://www.yageo.com/upload/media/product/productsearch/datasheet/rchip/PYu-RC_Group_51_RoHS_L_10.pdf
RESISTOR,66.5K OHM,0.063W,+/-0.1%,0603 | YAGEO_RMS1 | RT0603BRD0766K5L | 1 | R107 | Yageo | RT0603BRD0766K5L | RES SMD 66.5KOHM 0.1% 1/10W 0603 | Digi-Key | YAG1712CT-ND | https://www.yageo.com/upload/media/product/productsearch/datasheet/rchip/PYu-RT_1-to-0.01_RoHS_L_11.pdf
RESISTOR,100 OHM,0.063W,+/-1%, 0603 | BOURNS_RMS1 | CR0603-FX-1000ELF | 1 | R11 | Bourns Inc. | CR0603-FX-1000ELF | RES SMD 100 OHM 1% 1/10W 0603 | Digi-Key | CR0603-FX-1000ELFCT-ND | https://www.bourns.com/docs/Product-Datasheets/CHPREZTR.pdf
RESISTOR,1.5K OHM,0.250W,+/-1%,1206 | YAGEO_RMS1 | RC1206FR-071K5L | 1 | R114 | Yageo | RC1206FR-071K5L | RES SMD 1.5K OHM 1% 1/4W 1206 | Digi-Key | 311-1.50KFRCT-ND | https://www.yageo.com/upload/media/product/productsearch/datasheet/rchip/PYu-RC_Group_51_RoHS_L_10.pdf
RESISTOR,100 OHM,0.25W,+/-1%,1206 | YAGEO/PHYCOMP_RMS1 | 232272461001L | 1 | R116 | Yageo | RC1206FR-07100RL | RES SMD 100 OHM 1% 1/4W 1206 | Digi-Key | 311-100FRTR-ND | https://www.yageo.com/upload/media/product/productsearch/datasheet/rchip/PYu-RC_Group_51_RoHS_L_10.pdf
RESISTOR,270 OHM,0.125W,+/-1%,0805 | YAGEO_RMS1 | RC0805FR-07270RL | 1 | R117 | Yageo | RC0805FR-07270RL | RES SMD 270 OHM 1% 1/8W 0805 | Digi-Key | 311-270CRCT-ND | https://www.yageo.com/upload/media/product/productsearch/datasheet/rchip/PYu-RC_Group_51_RoHS_L_10.pdf
RESISTOR,470K OHM,0.063W,+/-1%,0603 | ASJ | CR16-4703FL | 2 | R118,R122 | Panasonic Electronic Components | ERJ-3EKF4703V | RES SMD 470K OHM 1% 1/10W 0603 | Digi-Key | P470KHCT-ND | https://industrial.panasonic.com/cdbs/www-data/pdf/RDA0000/AOA0000C304.pdf
RESISTOR, 22 K OHM,0.063W, +/-1%,0603 | SAMSUNG_RMS1 | RC1608F223ES | 1 | R119 | Panasonic Electronic Components | ERJ-3EKF2202V | RES SMD 22K OHM 1% 1/10W 0603 | Digi-Key | P22.0KHCT-ND | https://industrial.panasonic.com/cdbs/www-data/pdf/RDA0000/AOA0000C304.pdf
RESISTOR, 39K OHM, 0.063W, +/-0.1%, 0603 | YAGEO/PHYCOMP_RMS1 | RT0603BRD1339KL | 1 | R121 | Panasonic Electronic Components | ERA-3AEB393V | RES SMD 39K OHM 0.1% 1/10W 0603 | Digi-Key | P39KDBCT-ND | https://industrial.panasonic.com/cdbs/www-data/pdf/RDM0000/AOA0000C307.pdf
RESISTOR,470 OHM, 0.063W,+/-1%,0603 | YAGEO_RMS1 | RC0603FR-07470RL | 1 | R14 | Yageo | RC0603FR-07470RL | RES SMD 470 OHM 1% 1/10W 0603 | Digi-Key | 311-470HRCT-ND | https://www.yageo.com/upload/media/product/productsearch/datasheet/rchip/PYu-RC_Group_51_RoHS_L_10.pdf
RESISTOR,100KOHM,0.063W,+/-1%,0603 | YAGEO_RMS1 | 232270461004L | 15 | R15,R20,R31,R32,R42,R43,R53,R54,R58,R65,R94,R96,R97,R111,R123 | Yageo | RC0603FR-07100KL | RES SMD 100K OHM 1% 1/10W 0603 | Digi-Key | 311-100KHRTR-ND | https://www.yageo.com/upload/media/product/productsearch/datasheet/rchip/PYu-RC_Group_51_RoHS_L_10.pdf
RESISTOR,4.7KOHM,0.063W,+/-1% | YAGEO_RMS1 | RC0603FR-074K7L | 2 | R17,R26 | Yageo | RC0603FR-074K7L | RES SMD 4.7K OHM 1% 1/10W 0603 | Digi-Key | 311-4.70KHRCT-ND | https://www.yageo.com/upload/media/product/productsearch/datasheet/rchip/PYu-RC_Group_51_RoHS_L_10.pdf
RESISTOR,27K OHM, 0.063W, +/-1%, 0603 | YAGEO_RMS1 | 232270462703 | 1 | R18 | Panasonic Electronic Components | ERJ-3EKF2702V | RES SMD 27K OHM 1% 1/10W 0603 | Digi-Key | P27.0KHCT-ND | https://industrial.panasonic.com/cdbs/www-data/pdf/RDA0000/AOA0000C304.pdf
RESISTOR,110K OHM,0.603W,+/-0.1%,0603 | VISHAY_RMS1 | MCT06030D1103BP100 | 2 | R19,R33 | Panasonic Electronic Components | ERA-3AEB114V | RES SMD 110K OHM 0.1% 1/10W 0603 | Digi-Key | P110KDBCT-ND | https://industrial.panasonic.com/cdbs/www-data/pdf/RDM0000/AOA0000C307.pdf
RESISTOR,10.2K OHM, 0.063W, +/-0.1%,0603 | VISHAY_RMS1 | RV0603Y1022BNT | 1 | R2 | Panasonic Electronic Components | ERA-3AEB1022V | RES SMD 10.2KOHM 0.1% 1/10W 0603 | Digi-Key | P10.2KDBCT-ND | https://industrial.panasonic.com/cdbs/www-data/pdf/RDM0000/AOA0000C307.pdf
RESISTOR,470 OHM, 0.125W,+/-1%, 0805 | YAGEO_RMS1 | 232273464701L | 1 | R3 | Yageo | RC0805FR-07470RL | RES SMD 470 OHM 1% 1/8W 0805 | Digi-Key | 311-470CRTR-ND | https://www.yageo.com/upload/media/product/productsearch/datasheet/rchip/PYu-RC_Group_51_RoHS_L_10.pdf
RESISTOR,12K OHM,0.063W,+/-1%,0603 | VISHAY_RMS1 | CRCW060312K0FKEA | 1 | R4 | Vishay Dale | CRCW060312K0FKEA | RES SMD 12K OHM 1% 1/10W 0603 | Digi-Key | 541-12.0KHCT-ND | http://www.vishay.com/docs/20035/dcrcwe3.pdf
RESISTOR, 100K OHM, 0.063W,+/-0.1%,0603 | SUSUMU CO | RG1608P-104-B-T1 | 3 | R44,R64,R125 | Panasonic Electronic Components | ERA-3AEB104V | RES SMD 100K OHM 0.1% 1/10W 0603 | Digi-Key | P100KDBCT-ND | https://industrial.panasonic.com/cdbs/www-data/pdf/RDM0000/AOA0000C307.pdf
RESISTOR, 0.015 OHM, 1W,+/-1%,2010 | WELWYN | LRF2010-R015FW | 1 | R45 | Vishay Dale | WSL2010R0150FEA18 | RES 0.015 OHM 1% 1W 2010 | Digi-Key | WSLF-.015CT-ND | http://www.vishay.com/docs/31057/wslhigh.pdf
RESISTOR,39K OHM,0.063W,+/-1%,0603 | SAMSUNG_RMS1 | RC1608F393ES | 2 | R48,R61 | Panasonic Electronic Components | ERJ-3EKF3902V | RES SMD 39K OHM 1% 1/10W 0603 | Digi-Key | P39.0KHCT-ND | https://industrial.panasonic.com/cdbs/www-data/pdf/RDA0000/AOA0000C304.pdf
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

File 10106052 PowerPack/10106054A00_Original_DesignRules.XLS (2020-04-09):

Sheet: Design Rules Export
Name | Priority | Enabled | Type | Category | Scope | Attributes
AssemblyTestpoint | 1 | True | Assembly Testpoint Style | Testpoint | All | Under Comp - Allow Sides - Top, Bottom Pref
 |  |  |  |  |  | Size = 1.524mm Pref Hole Size = 0.813mm |  | NetClass 0.6mm Nets
 |  |  |  |  |  | Using Grid = Yes Grid = 0.025mm Grid | Pcbnew | Name | Node Count | Signal Length (mil) | Total Pin/Package Length (mil) | Routed Length (mil) | Unrouted (Manhattan) (mil)
 |  |  |  |  |  | Tolerance = 0mm
AssemblyTestPointUsage | 1 | True | Assembly Testpoint Usage | Testpoint | All | Testpoint - One Required Multiple - Not Allowed |  | +3.0VREF | 6 | n/a | 0 | 4005.154 | 0
Clearance - NetClass - | 1 | True | Clearance | Electrical | InNetClass('ClearanceClass_3(RuleSet)') - All | Generic clearance = 0.25mm, and 10 value(s) for objects |  | +5V | 21 | n/a | 0 | 16536.326 | 0
ClearanceClass_3(RuleSet) |  |  |  |  |  |  |  | =+VDC_PERM | 9 | n/a | 0 | 7040.1 | 0
ComponentClearance - Default - | 1 | True | Component Clearance | Placement | All - All | Horizontal Clearance = 0.152mm Vertical |  | CHARG_BAT1 | 3 | n/a | 0 | 3773.518 | 0
DEFAULT |  |  |  |  |  | Clearance = 0.254mm |  | CHARG_BAT2 | 3 | n/a | 0 | 2089.695 | 0
Default Impedance | 1 | True | Impedance | Signal Integrity | All | Min = 50.00 Max = 150.0 |  | DISCH_BAT1 | 3 | n/a | 0 | 3624.911 | 0
Default Length | 1 | True | Length | High Speed | All | Min Length = 0mm Max Length = 1270mm |  | DISCH_BAT2 | 3 | n/a | 0 | 1853.427 | 0
Default Parallel Segment Adjasent | 1 | True | Parallel Segment | High Speed | All - All | Gap = 5.08mm Limit = 25.4mm Layer - Adjacent Layer | D9-Pad2 | N16098669 | 6 | n/a | 0 | 1529.863 | 0
Default Routing Topology | 1 | True | Routing Topology | Routing | All | Topology - Shortest | D1-Pad2 | N16099189 | 7 | n/a | 0 | 1290.307 | 0
DiffPairsRouting | 1 | True | Differential Pairs Routing | Routing | All | Pref Gap = 0.254mm Min Gap = 0.254mm Max | T2-Pad4 | N16099574 | 2 | 344.488 | 0 | 525.732 | 0
 |  |  |  |  |  | Gap = 0.254mmPref Width = 0.381mm Min Width | D6-Pad1 | N16102968 | 7 | n/a | 0 | 1532.975 | 0
 |  |  |  |  |  | = 0.381mm Max Width = 0.381mm | T8-Pad4 | N16103052 | 2 | 344.488 | 0 | 547.456 | 0
FabricationTestpoint | 1 | True | Fabrication Testpoint Style | Testpoint | All | Under Comp - Allow Sides - Top, Bottom Pref | +BATT_BUS | N16104931 | 8 | n/a | 0 | 2976.663 | 0
 |  |  |  |  |  | Size = 1.524mm Pref Hole Size = 0.813mm | C8-Pad1 | N16104935 | 7 | n/a | 0 | 3498.897 | 0
 |  |  |  |  |  | Using Grid = Yes Grid = 0.025mm Grid Tolerance = 0mm | FL1-PadB | N16275854 | 2 | 709.815 | 0 | 718.815 | 0
FabricationTestPointUsage | 1 | True | Fabrication Testpoint Usage | Testpoint | All | Testpoint - One Required Multiple - Not Allowed | FL1-PadPSG | N16275858 | 2 | 566.677 | 0 | 883.609 | 0
Fanout_Small | 1 | True | Fanout Control | Routing | (CompPinCount < 5) | Style - Auto Direction - Out Then In Via Grid =0.025mm | F1-Pad1 | N16293601 | 2 | 178.127 | 0 | 384.644 | 0
Height | 1 | True | Height | Placement | All | Pref Height = 12.7mm Min Height = 0mm Max |  | V_CH | 4 | n/a | 0 | 6471.47 | 0
 |  |  |  |  |  | Height = 25.4mm |  | V_DC_CHARGER | 5 | n/a | 0 | 7976.484 | 0
HoleSize | 1 | True | Hole Size | Manufacturing | All | Min = 0.025mm Max = 2.54mm |  | V_EN | 3 | n/a | 0 | 4962.133 | 0
HoleToHoleClearance - Default - | 1 | True | Hole To Hole Clearance | Manufacturing | All - All | Hole To Hole Clearance = 0.152mm |  | X00088 | 2 | 413.118 | 0 | 422.118 | 0
DEFAULT |  |  |  |  |  |  |  | X00089 | 4 | n/a | 0 | 788.915 | 0
LayerPairs | 1 | True | Layer Pairs | Manufacturing | All | Layer Pairs - Enforce
MinimumSolderMaskSliver | 1 | True | Minimum Solder Mask Sliver | Manufacturing | All - All | Minimum Solder Mask Sliver = 0.254mm
NetAntennae | 1 | True | Net Antennae | Manufacturing | All | Net Antennae Tolerance = 0mm |  | ClearanceClass_3(RuleSet)
PasteMaskExpansion | 1 | True | Paste Mask Expansion | Mask | All | Expansion = 0mm |  | AGND | 21 | n/a | 0 | 11568.952 | 0
PlaneClearance - FootPrint 'CAPPRD350W60D800H1250PAAA' | 1 | True | Power Plane Clearance | Plane | HasFootprint('CAPPRD350W60D800H1250PAAA') | Clearance = 0.4mm |  | GND | 52 | n/a | 0 | 18985.964 | 3298.384
PlaneConnect - FootPrint 'CAPPRD350W60D800H1250P' | 1 | True | Power Plane Connect Style | Plane | HasFootprint('CAPPRD350W60D800H1250P') | Style - Relief Connect Expansion = 0.25mm
 |  |  |  |  |  | Width = 0.4mm Gap = 0.15mm # Entries = 4
PolygonConnect - FootPrint 'CON-43650-0229'_10 | 1 | True | Polygon Connect Style | Plane | HasFootprint('CON-43650-0229') - All | Style - Relief Connect Width = 0.45mm Angle =
 |  |  |  |  |  | 45 # Entries = 4 Air Gap = 0.15mm
Room: DRW82330104 | 1 | True | Room Definition | Placement | All | Region (BR) = (200mm, 0mm), (210mm, 4mm)
 |  |  |  |  |  | Style - Keep Outside
RoutingCorners | 1 | True | Routing Corners | Routing | All | Style - 45 Degree Min Setback = 2.54mm Max
 |  |  |  |  |  | Setback = 2.54mm
RoutingLayers - Default - DEFAULT | 1 | True | Routing Layers | Routing | All | TopLayer - Enabled BottomLayer - Enabled
RoutingPriority - Default - DEFAULT | 1 | True | Routing Priority | Routing | All | Priority = 3
RoutingVias - Default - DEFAULT | 1 | True | Routing Via Style | Routing | All | Pref Size = 1mm Pref Hole Size = 0.4mm
ShortCircuit | 1 | True | Short-Circuit | Electrical | All - All | Short Circuit - Not Allowed
SilkToSilkClearance | 1 | True | Silk To Silk Clearance | Manufacturing | All - All | Silk to Silk Clearance = 0.254mm
SilkToSolderMaskClearance | 1 | True | Silk To Solder Mask Clearance | Manufacturing | IsPad - All | Silk To Solder Mask Clearance = 0.254mm
SMDToCorner - Default - DEFAULT | 1 | True | SMD To Corner | SMT | All | Distance = 0.152mm
SolderMaskExpansion from CAM settings | 1 | True | Solder Mask Expansion | Mask | All | Expansion = 0.025mm
UnpouredPolygon | 1 | True | Modified Polygon | Electrical | All | Allow modified - No Allow shelved - No
UnRoutedNet | 1 | True | Un-Routed Net | Electrical | All | (No Attributes)
Width - NetClass - | 1 | True | Width | Routing | InNetClass('ClearanceClass_3(RuleSet)') | Pref Width = 0.6mm Min Width = 0.25mm Max
ClearanceClass_3(RuleSet) |  |  |  |  |  | Width = 1mm
Clearance - NetClass - 0.6MM | 2 | True | Clearance | Electrical | InNetClass('0.6MM') - All | Generic clearance = 0.5mm, and 10 value(s) for
 |  |  |  |  |  | objects
Default Parallel Segment Same Layer | 2 | True | Parallel Segment | High Speed | All - All | Gap = 5.08mm Limit = 25.4mm Layer - Same
 |  |  |  |  |  | Layer
Fanout_SOIC | 2 | True | Fanout Control | Routing | IsSOIC | Style - Auto Direction - Alternating In and Out Via
 |  |  |  |  |  | Grid = 0.025mm
PlaneClearance - FootPrint 'CAPPRD350W60D800H1250PAAAA' | 2 | True | Power Plane Clearance | Plane | HasFootprint('CAPPRD350W60D800H1250PAAAA') | Clearance = 0.4mm
PlaneConnect - FootPrint 'CAPPRD350W60D800H1250P'_12 | 2 | True | Power Plane Connect Style | Plane | HasFootprint('CAPPRD350W60D800H1250P') | Style - Relief Connect Expansion = 0.25mm
 |  |  |  |  |  | Width = 0.4mm Gap = 0.15mm # Entries = 4
PolygonConnect - FootPrint 'CON-43650-0229'_11 | 2 | True | Polygon Connect Style | Plane | HasFootprint('CON-43650-0229') - All | Style - Relief Connect Width = 0.45mm Angle =
 |  |  |  |  |  | 45 # Entries = 4 Air Gap = 0.15mm
Room: DRW62746091 | 2 | True | Room Definition | Placement | All | Region (BR) = (126mm, 0mm), (154mm, 4mm)
 |  |  |  |  |  | Style - Keep Outside
Width - NetClass - 0.6MM | 2 | True | Width | Routing | InNetClass('0.6MM') | Pref Width = 0.6mm Min Width = 0.25mm Max
 |  |  |  |  |  | Width = 5mm
Clearance - Default - DEFAULT - Via | 3 | True | Clearance | Electrical | IsVia - IsVia | Clearance = 0.152mm
Default Width | 3 | True | Width | Routing | All | Pref Width = 0.25mm Min Width = 0.25mm Max
 |  |  |  |  |  | Width = 1mm
Fanout_LCC | 3 | True | Fanout Control | Routing | IsLCC | Style - Auto Direction - Alternating In and Out Via
 |  |  |  |  |  | Grid = 0.025mm
PlaneClearance - FootPrint 'CAPPRD350W60D800H1250PAAAAA' | 3 | True | Power Plane Clearance | Plane | HasFootprint('CAPPRD350W60D800H1250PAAAAA') | Clearance = 0.4mm
PlaneConnect - FootPrint 'CAPPRD350W60D800H1250PA' | 3 | True | Power Plane Connect Style | Plane | HasFootprint('CAPPRD350W60D800H1250PA') | Style - Relief Connect Expansion = 0.25mm
 |  |  |  |  |  | Width = 0.4mm Gap = 0.15mm # Entries = 4
PolygonConnect - FootPrint 'STAR' | 3 | True | Polygon Connect Style | Plane | HasFootprint('STAR') - All | Style - Relief Connect Width = 0.25mm Angle =
 |  |  |  |  |  | 45 # Entries = 4 Air Gap = 0.2mm
Room: DRW59518629 | 3 | True | Room Definition | Placement | All | Region (BR) = (0mm, 0mm), (11mm, 4mm) Style -
 |  |  |  |  |  | Keep Outside
Clearance - Default - DEFAULT- SMD | 4 | True | Clearance | Electrical | IsVia - IsSMTPin | Clearance = 0.152mm
Fanout_BGA | 4 | True | Fanout Control | Routing | IsBGA | Style - Auto Direction - Alternating In and Out Via
 |  |  |  |  |  | Grid = 0.025mm
PlaneClearance - FootPrint 'CAPPRD350W60D800H1250P' | 4 | True | Power Plane Clearance | Plane | HasFootprint('CAPPRD350W60D800H1250P') | Clearance = 0.4mm
PlaneConnect - FootPrint 'CAPPRD350W60D800H1250PAAA' | 4 | True | Power Plane Connect Style | Plane | HasFootprint('CAPPRD350W60D800H1250PAAA') | Style - Relief Connect Expansion = 0.25mm
 |  |  |  |  |  | Width = 0.4mm Gap = 0.15mm # Entries = 4
PolygonConnect - FootPrint 'CAPPRD350W60D800H1250PAAAA'_6 | 4 | True | Polygon Connect Style | Plane | HasFootprint('CAPPRD350W60D800H1250PAAAA') - All | Style - Relief Connect Width = 0.4mm Angle =
 |  |  |  |  |  | 45 # Entries = 4 Air Gap = 0.15mm
Room: DRW49464876 | 4 | True | Room Definition | Placement | All | Region (BR) = (199mm, 0mm), (210mm, 4.5mm)
 |  |  |  |  |  | Style - Keep Outside
Clearance - Default - DEFAULT - Net | 5 | True | Clearance | Electrical | All - All | Generic clearance = 0.25mm, and 13 value(s) for
 |  |  |  |  |  | objects
Fanout_Default | 5 | True | Fanout Control | Routing | All | Style - Auto Direction - Alternating In and Out Via
 |  |  |  |  |  | Grid = 0.025mm
PlaneClearance - FootPrint 'CAPPRD350W60D800H1250PA' | 5 | True | Power Plane Clearance | Plane | HasFootprint('CAPPRD350W60D800H1250PA') | Clearance = 0.4mm
PlaneConnect - FootPrint 'CAPPRD350W60D800H1250PAAA'_15 | 5 | True | Power Plane Connect Style | Plane | HasFootprint('CAPPRD350W60D800H1250PAAA') | Style - Relief Connect Expansion = 0.25mm
 |  |  |  |  |  | Width = 0.4mm Gap = 0.15mm # Entries = 4
PolygonConnect - FootPrint 'CAPPRD350W60D800H1250PAAAAA' | 5 | True | Polygon Connect Style | Plane | HasFootprint('CAPPRD350W60D800H1250PAAAAA') - All | Style - Relief Connect Width = 0.4mm Angle =
 |  |  |  |  |  | 45 # Entries = 4 Air Gap = 0.15mm
Room: DRW38183478 | 5 | True | Room Definition | Placement | All | Region (BR) = (11.6mm, 29mm), (16.1mm, 34mm)
 |  |  |  |  |  | Style - Keep Outside
PlaneClearance - FootPrint 'CAPPRD350W60D800H1250PAA' | 6 | True | Power Plane Clearance | Plane | HasFootprint('CAPPRD350W60D800H1250PAA') | Clearance = 0.4mm
PlaneConnect - FootPrint 'CAPPRD350W60D800H1250PAAAA' | 6 | True | Power Plane Connect Style | Plane | HasFootprint('CAPPRD350W60D800H1250PAAAA') | Style - Relief Connect Expansion = 0.25mm
 |  |  |  |  |  | Width = 0.4mm Gap = 0.15mm # Entries = 4
PolygonConnect - FootPrint 'CAPPRD350W60D800H1250PAAAAA'_7 | 6 | True | Polygon Connect Style | Plane | HasFootprint('CAPPRD350W60D800H1250PAAAAA') - All | Style - Relief Connect Width = 0.4mm Angle =
 |  |  |  |  |  | 45 # Entries = 4 Air Gap = 0.15mm
Room: DRW38138637 | 6 | True | Room Definition | Placement | All | Region (BR) = (53.5mm, 0mm), (73.5mm, 4mm)
 |  |  |  |  |  | Style - Keep Outside
PlaneClearance - FootPrint 'CON2PHDR1000W777L396P' | 7 | True | Power Plane Clearance | Plane | HasFootprint('CON2PHDR1000W777L396P') | Clearance = 0.05mm
PlaneConnect - FootPrint 'CAPPRD350W60D800H1250PA'_13 | 7 | True | Power Plane Connect Style | Plane | HasFootprint('CAPPRD350W60D800H1250PA') | Style - Relief Connect Expansion = 0.25mm
 |  |  |  |  |  | Width = 0.4mm Gap = 0.15mm # Entries = 4
PolygonConnect - FootPrint 'CAPPRD350W60D800H1250PAAA' | 7 | True | Polygon Connect Style | Plane | HasFootprint('CAPPRD350W60D800H1250PAAA') - All | Style - Relief Connect Width = 0.4mm Angle =
 |  |  |  |  |  | 45 # Entries = 4 Air Gap = 0.15mm
Room: DRW37987174 | 7 | True | Room Definition | Placement | All | Region (BR) = (157mm, 29mm), (161.5mm, 34mm)
 |  |  |  |  |  | Style - Keep Outside
PlaneClearance - FootPrint 'CON-43650-0229' | 8 | True | Power Plane Clearance | Plane | HasFootprint('CON-43650-0229') | Clearance = 0.4mm
PlaneConnect - FootPrint 'CAPPRD350W60D800H1250PAA' | 8 | True | Power Plane Connect Style | Plane | HasFootprint('CAPPRD350W60D800H1250PAA') | Style - Relief Connect Expansion = 0.25mm
 |  |  |  |  |  | Width = 0.4mm Gap = 0.15mm # Entries = 4
PolygonConnect - FootPrint 'CAPPRD350W60D800H1250PAAA'_5 | 8 | True | Polygon Connect Style | Plane | HasFootprint('CAPPRD350W60D800H1250PAAA') - All | Style - Relief Connect Width = 0.4mm Angle =
 |  |  |  |  |  | 45 # Entries = 4 Air Gap = 0.15mm
Room: DRW20101131 | 8 | True | Room Definition | Placement | All | Region (BR) = (71.8mm, 29mm), (76.3mm, 34mm)
 |  |  |  |  |  | Style - Keep Outside
PlaneClearance - FootPrint 'STAR' | 9 | True | Power Plane Clearance | Plane | HasFootprint('STAR') | Clearance = 0.475mm
PlaneConnect - FootPrint 'CAPPRD350W60D800H1250PAA'_14 | 9 | True | Power Plane Connect Style | Plane | HasFootprint('CAPPRD350W60D800H1250PAA') | Style - Relief Connect Expansion = 0.25mm
 |  |  |  |  |  | Width = 0.4mm Gap = 0.15mm # Entries = 4
PolygonConnect - FootPrint 'CAPPRD350W60D800H1250PAAAA' | 9 | True | Polygon Connect Style | Plane | HasFootprint('CAPPRD350W60D800H1250PAAAA') - All | Style - Relief Connect Width = 0.4mm Angle =
 |  |  |  |  |  | 45 # Entries = 4 Air Gap = 0.15mm
PlaneClearance - FootPrint 'CAPPRD350W60D800H1250PB' | 10 | True | Power Plane Clearance | Plane | HasFootprint('CAPPRD350W60D800H1250PB') | Clearance = 0.4mm
PlaneConnect - FootPrint 'CAPPRD350W60D800H1250PB' | 10 | True | Power Plane Connect Style | Plane | HasFootprint('CAPPRD350W60D800H1250PB') | Style - Relief Connect Expansion = 0.25mm
 |  |  |  |  |  | Width = 0.4mm Gap = 0.15mm # Entries = 4
PolygonConnect - FootPrint 'CAPPRD350W60D800H1250PBA'_9 | 10 | True | Polygon Connect Style | Plane | HasFootprint('CAPPRD350W60D800H1250PBA') - All | Style - Relief Connect Width = 0.4mm Angle =
 |  |  |  |  |  | 45 # Entries = 4 Air Gap = 0.15mm
PlaneClearance - FootPrint 'CAPPRD350W60D800H1250PBA' | 11 | True | Power Plane Clearance | Plane | HasFootprint('CAPPRD350W60D800H1250PBA') | Clearance = 0.4mm
PlaneConnect - FootPrint 'CAPPRD350W60D800H1250PB'_18 | 11 | True | Power Plane Connect Style | Plane | HasFootprint('CAPPRD350W60D800H1250PB') | Style - Relief Connect Expansion = 0.25mm
 |  |  |  |  |  | Width = 0.4mm Gap = 0.15mm # Entries = 4
PolygonConnect - FootPrint 'CON254W80L508T254H600P' | 11 | True | Polygon Connect Style | Plane | HasFootprint('CON254W80L508T254H600P') - All | Style - Relief Connect Width = 0.45mm Angle =
 |  |  |  |  |  | 45 # Entries = 4 Air Gap = 0.15mm
PlaneClearance - FootPrint 'CON254W80L508T254H600P' | 12 | True | Power Plane Clearance | Plane | HasFootprint('CON254W80L508T254H600P') | Clearance = 0.4mm
PlaneConnect - FootPrint 'CAPPRD350W60D800H1250PBA' | 12 | True | Power Plane Connect Style | Plane | HasFootprint('CAPPRD350W60D800H1250PBA') | Style - Relief Connect Expansion = 0.25mm
 |  |  |  |  |  | Width = 0.4mm Gap = 0.15mm # Entries = 4
PolygonConnect - FootPrint 'CON-43650-0229' | 12 | True | Polygon Connect Style | Plane | HasFootprint('CON-43650-0229') - All | Style - Relief Connect Width = 0.45mm Angle =
 |  |  |  |  |  | 45 # Entries = 4 Air Gap = 0.15mm
PlaneConnect - FootPrint 'CAPPRD350W60D800H1250PAAAA'_16 | 13 | True | Power Plane Connect Style | Plane | HasFootprint('CAPPRD350W60D800H1250PAAAA') | Style - Relief Connect Expansion = 0.25mm
 |  |  |  |  |  | Width = 0.4mm Gap = 0.15mm # Entries = 4
PolygonConnect - FootPrint 'CAPPRD350W60D800H1250PB' | 13 | True | Polygon Connect Style | Plane | HasFootprint('CAPPRD350W60D800H1250PB') - All | Style - Relief Connect Width = 0.4mm Angle =
 |  |  |  |  |  | 45 # Entries = 4 Air Gap = 0.15mm
PlaneConnect - FootPrint 'CAPPRD350W60D800H1250PAAAAA' | 14 | True | Power Plane Connect Style | Plane | HasFootprint('CAPPRD350W60D800H1250PAAAAA') | Style - Relief Connect Expansion = 0.25mm
 |  |  |  |  |  | Width = 0.4mm Gap = 0.15mm # Entries = 4
PolygonConnect - FootPrint 'CAPPRD350W60D800H1250PB'_8 | 14 | True | Polygon Connect Style | Plane | HasFootprint('CAPPRD350W60D800H1250PB') - All | Style - Relief Connect Width = 0.4mm Angle =
 |  |  |  |  |  | 45 # Entries = 4 Air Gap = 0.15mm
PlaneConnect - FootPrint'CAPPRD350W60D800H1250PAAAAA'_17 | 15 | True | Power Plane Connect Style | Plane | HasFootprint('CAPPRD350W60D800H1250PAAAAA') | Style - Relief Connect Expansion = 0.25mm
 |  |  |  |  |  | Width = 0.4mm Gap = 0.15mm # Entries = 4
PolygonConnect - FootPrint 'CAPPRD350W60D800H1250PBA' | 15 | True | Polygon Connect Style | Plane | HasFootprint('CAPPRD350W60D800H1250PBA') - All | Style - Relief Connect Width = 0.4mm Angle =
 |  |  |  |  |  | 45 # Entries = 4 Air Gap = 0.15mm
PlaneConnect - FootPrint 'CON-43650-0229'_20 | 16 | True | Power Plane Connect Style | Plane | HasFootprint('CON-43650-0229') | Style - Relief Connect Expansion = 0.1mm Width
 |  |  |  |  |  | = 0.45mm Gap = 0.15mm # Entries = 4
PolygonConnect - FootPrint 'CAPPRD350W60D800H1250PAA'_4 | 16 | True | Polygon Connect Style | Plane | HasFootprint('CAPPRD350W60D800H1250PAA') - All | Style - Relief Connect Width = 0.4mm Angle =
 |  |  |  |  |  | 45 # Entries = 4 Air Gap = 0.15mm
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

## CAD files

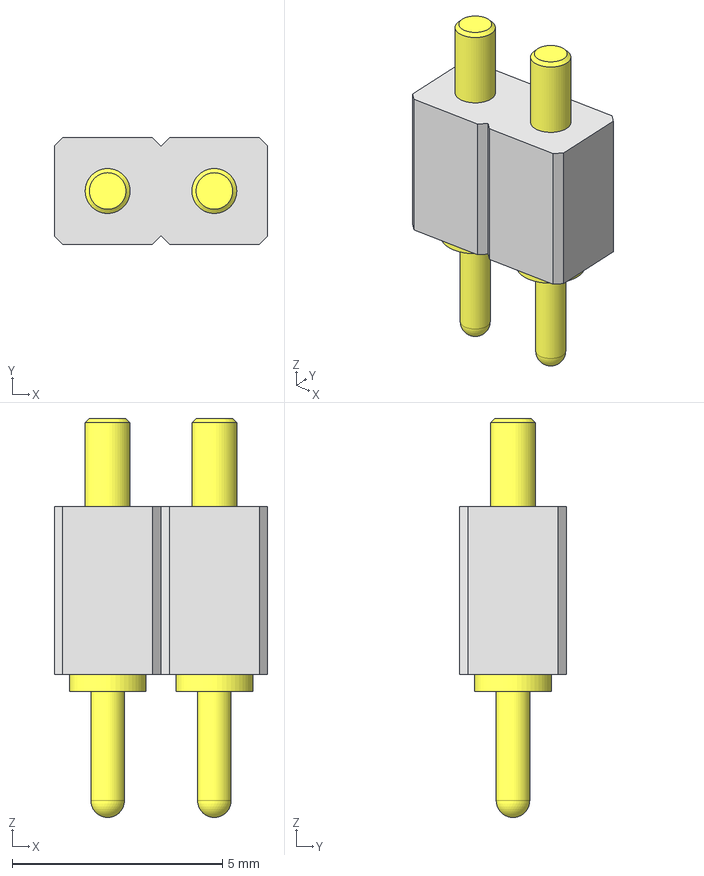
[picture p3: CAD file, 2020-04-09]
10106052 PowerPack/3D Models/5078_ACP-D-254-1-02-65.stp
5.08 x 2.54 x 9.50 mm
Broche contact à piston x 2
Isolant standard

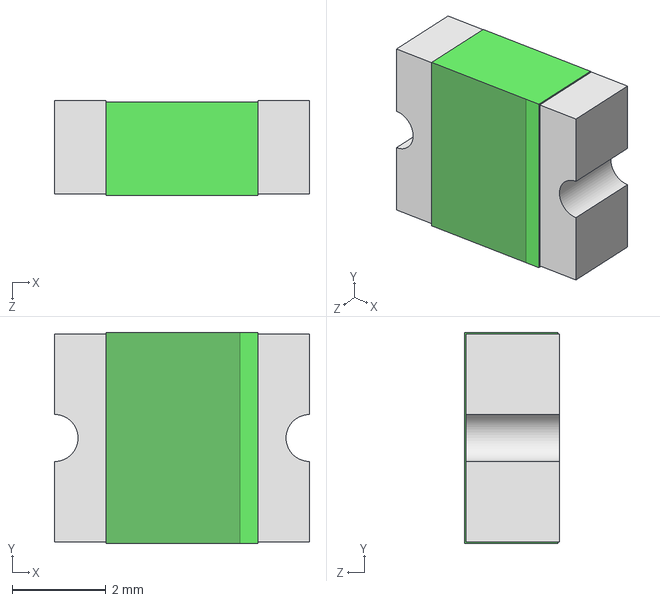
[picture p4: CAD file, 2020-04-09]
10106052 PowerPack/3D Models/Fuse 2016L.step
5.44 x 4.51 x 2.03 mm

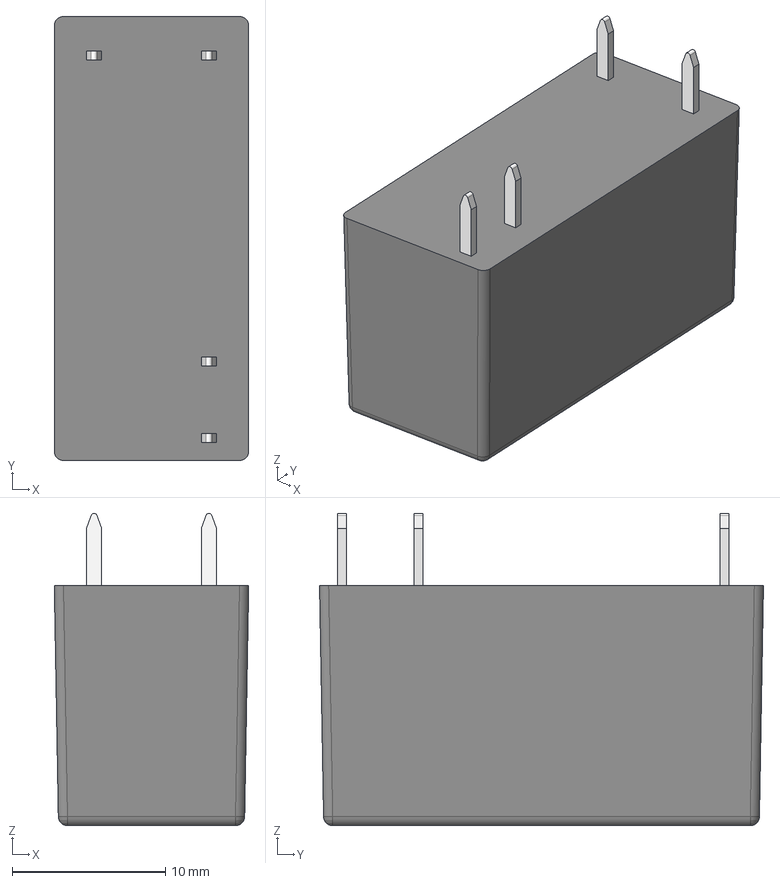
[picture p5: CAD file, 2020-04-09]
10106052 PowerPack/3D Models/4181.stp
12.7 x 29.0 x 20.4 mm

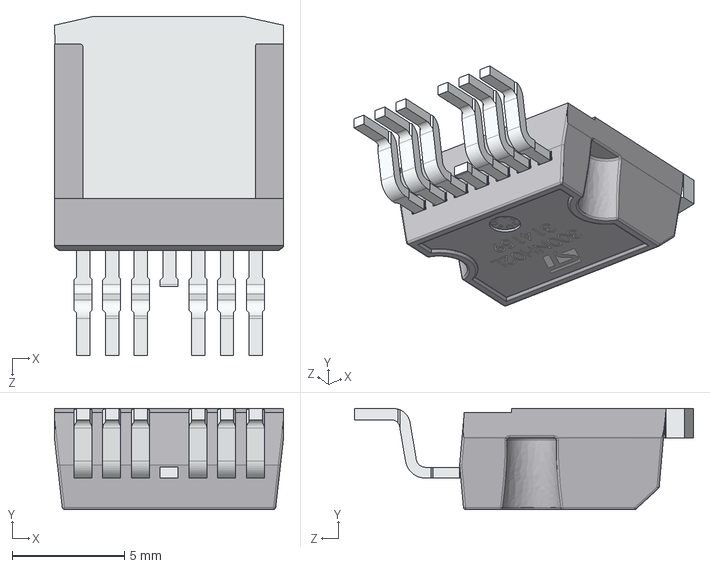
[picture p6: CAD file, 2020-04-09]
10106052 PowerPack/3D Models/d2pak7_ST.STEP
10.2 x 4.50 x 15.1 mm

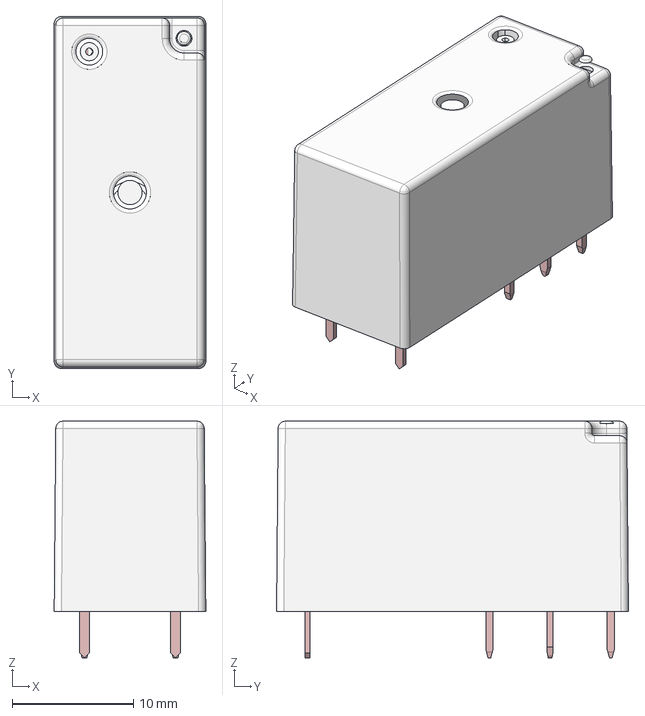
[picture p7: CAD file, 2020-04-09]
10106052 PowerPack/3D Models/4152 v1.step
12.5 x 29.0 x 19.5 mm

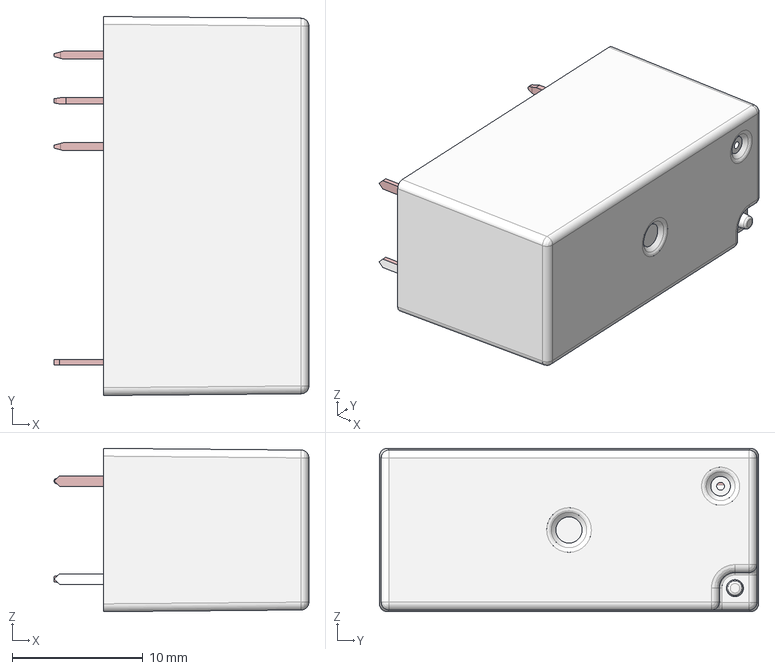
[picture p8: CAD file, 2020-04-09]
10106052 PowerPack/3D Models/4131.stp
19.5 x 29.0 x 12.5 mm

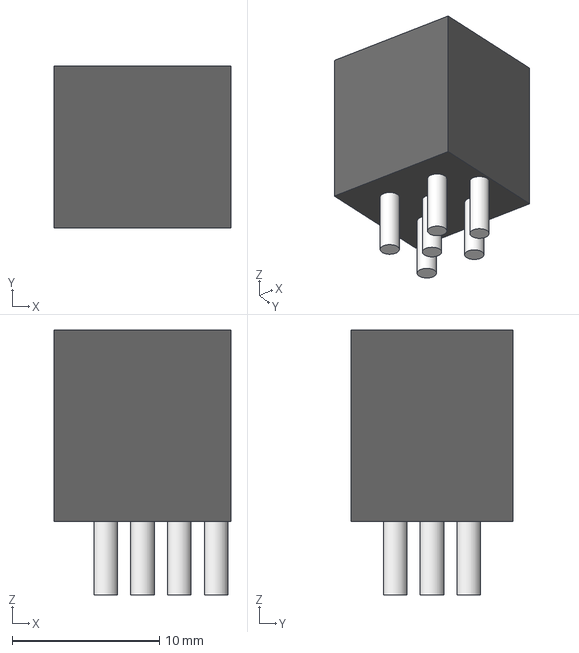
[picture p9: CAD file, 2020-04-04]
10106052 PowerPack/3D Models/BNX002-01.step
12.0 x 11.0 x 18.0 mm

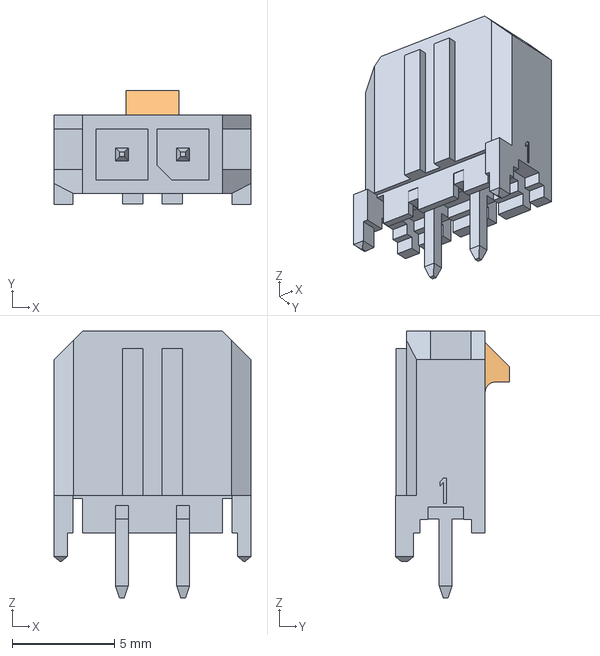
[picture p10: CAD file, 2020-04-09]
10106052 PowerPack/3D Models/436500229.stp
9.65 x 5.61 x 13.1 mm

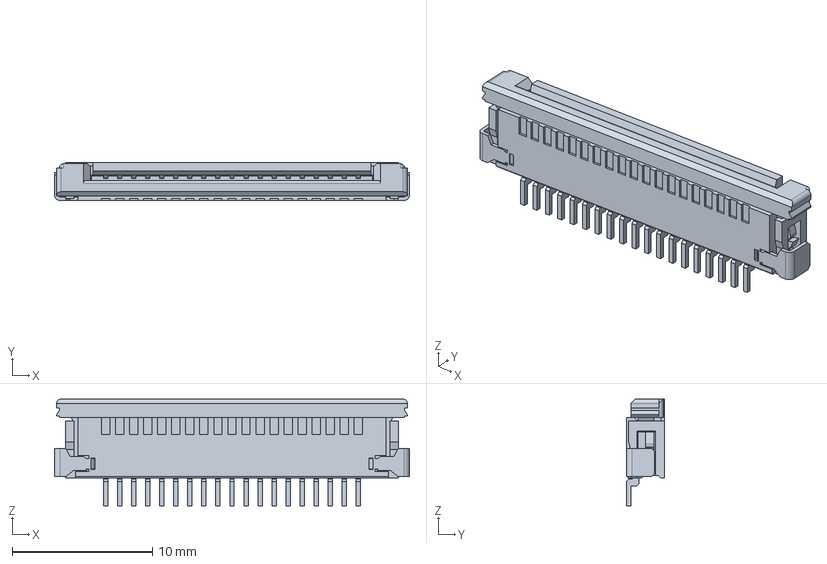
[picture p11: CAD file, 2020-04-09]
10106052 PowerPack/3D Models/522071960.stp
25.3 x 2.70 x 7.60 mm

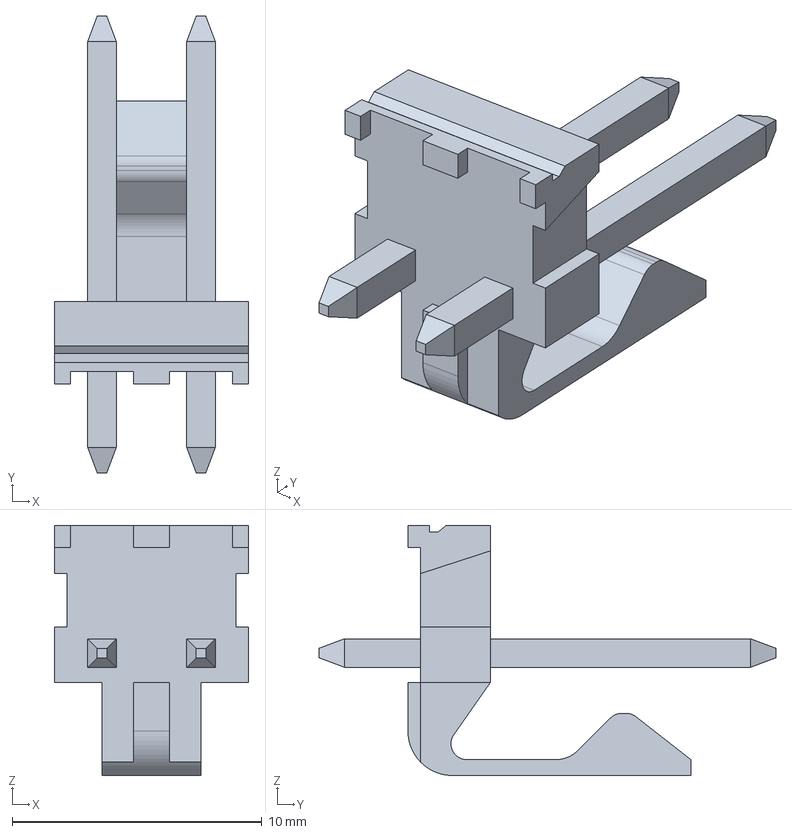
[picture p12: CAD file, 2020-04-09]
10106052 PowerPack/3D Models/026614020.stp
7.77 x 18.3 x 10.0 mm

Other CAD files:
10106052 PowerPack/3D Models/4152.stp
10106052 PowerPack/3D Models/4161.stp

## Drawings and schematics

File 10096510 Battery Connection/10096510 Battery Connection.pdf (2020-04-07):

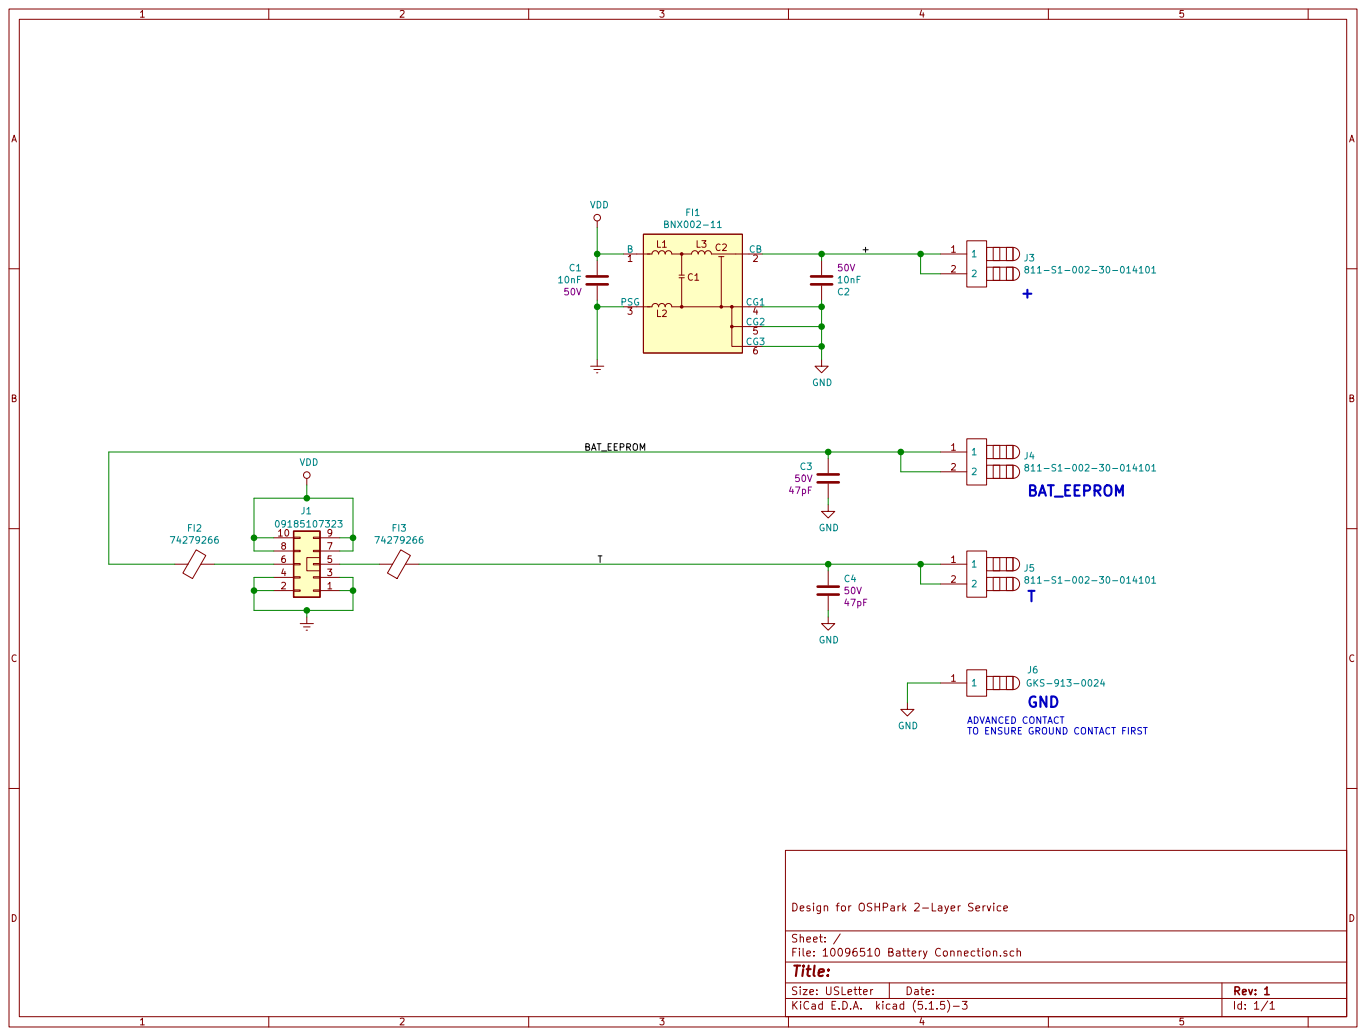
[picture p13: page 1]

File: 10096510 Battery Connection.sch Sheet: / Design for OSHPark 2-Layer Service

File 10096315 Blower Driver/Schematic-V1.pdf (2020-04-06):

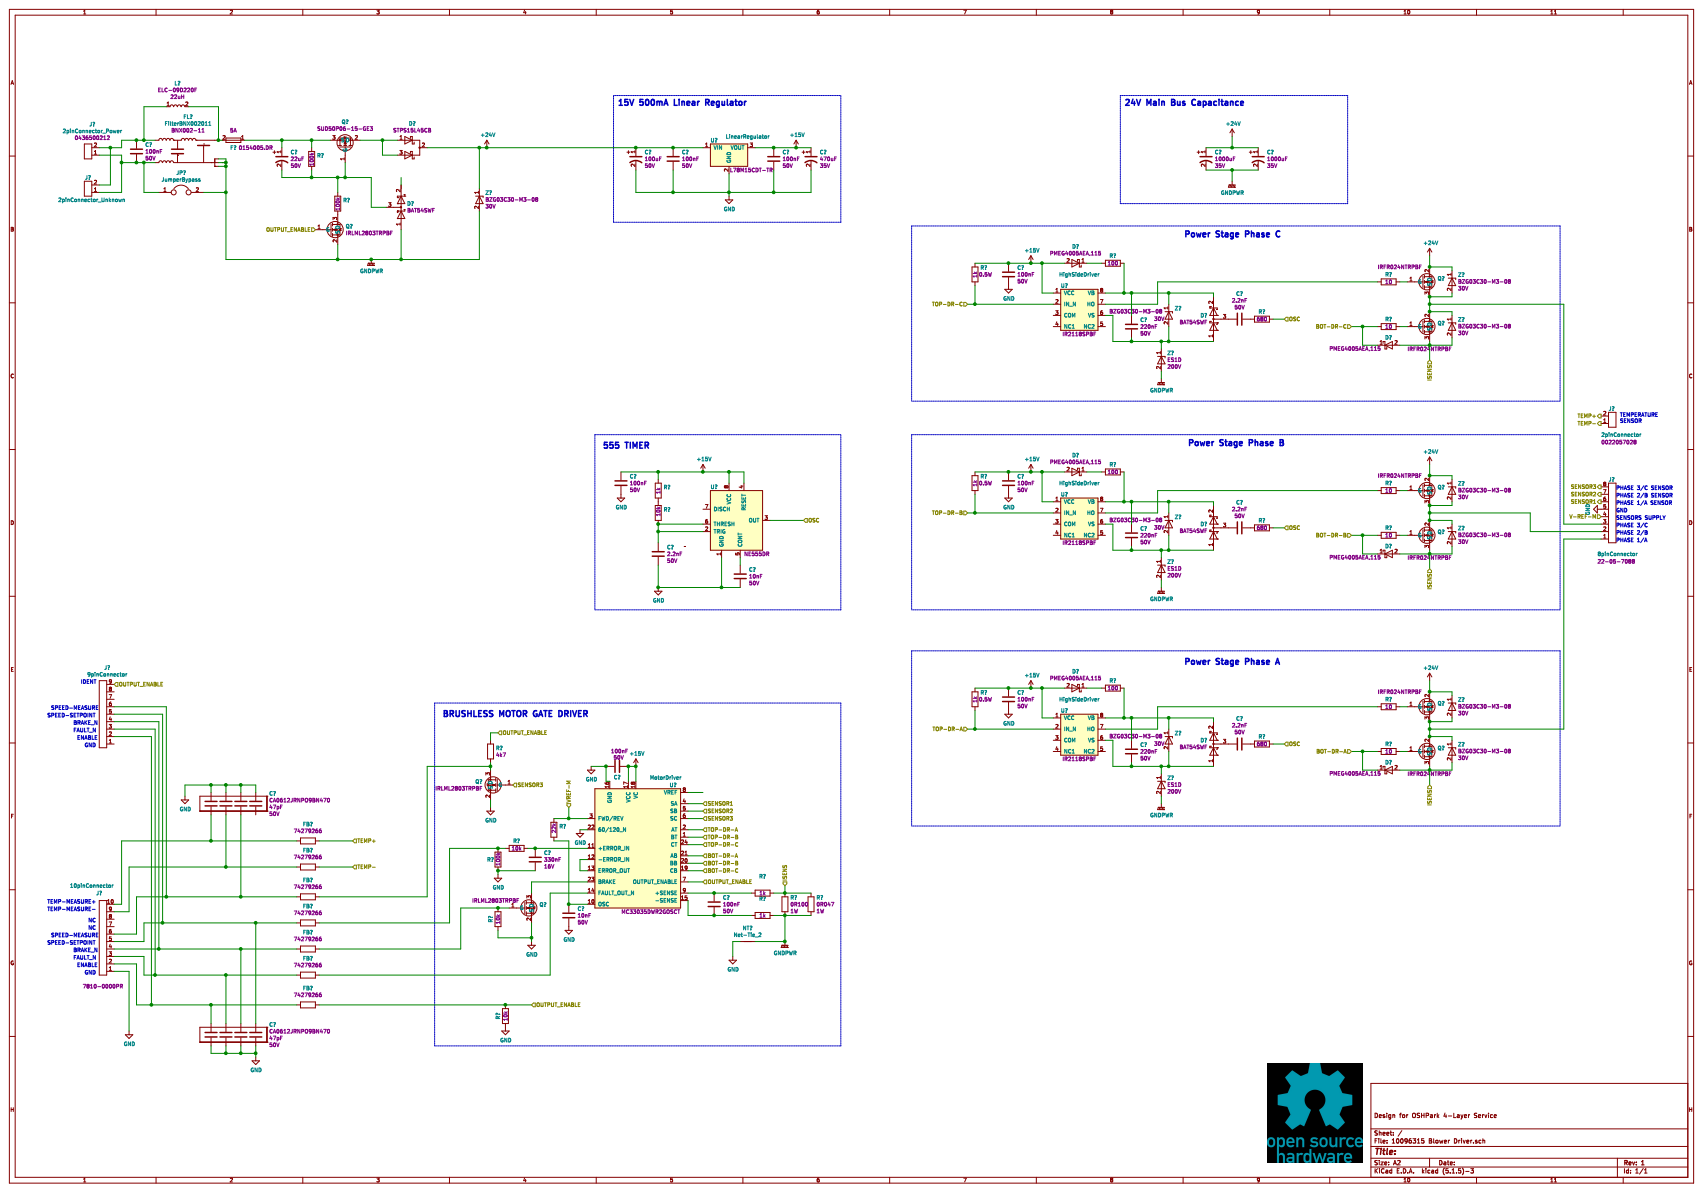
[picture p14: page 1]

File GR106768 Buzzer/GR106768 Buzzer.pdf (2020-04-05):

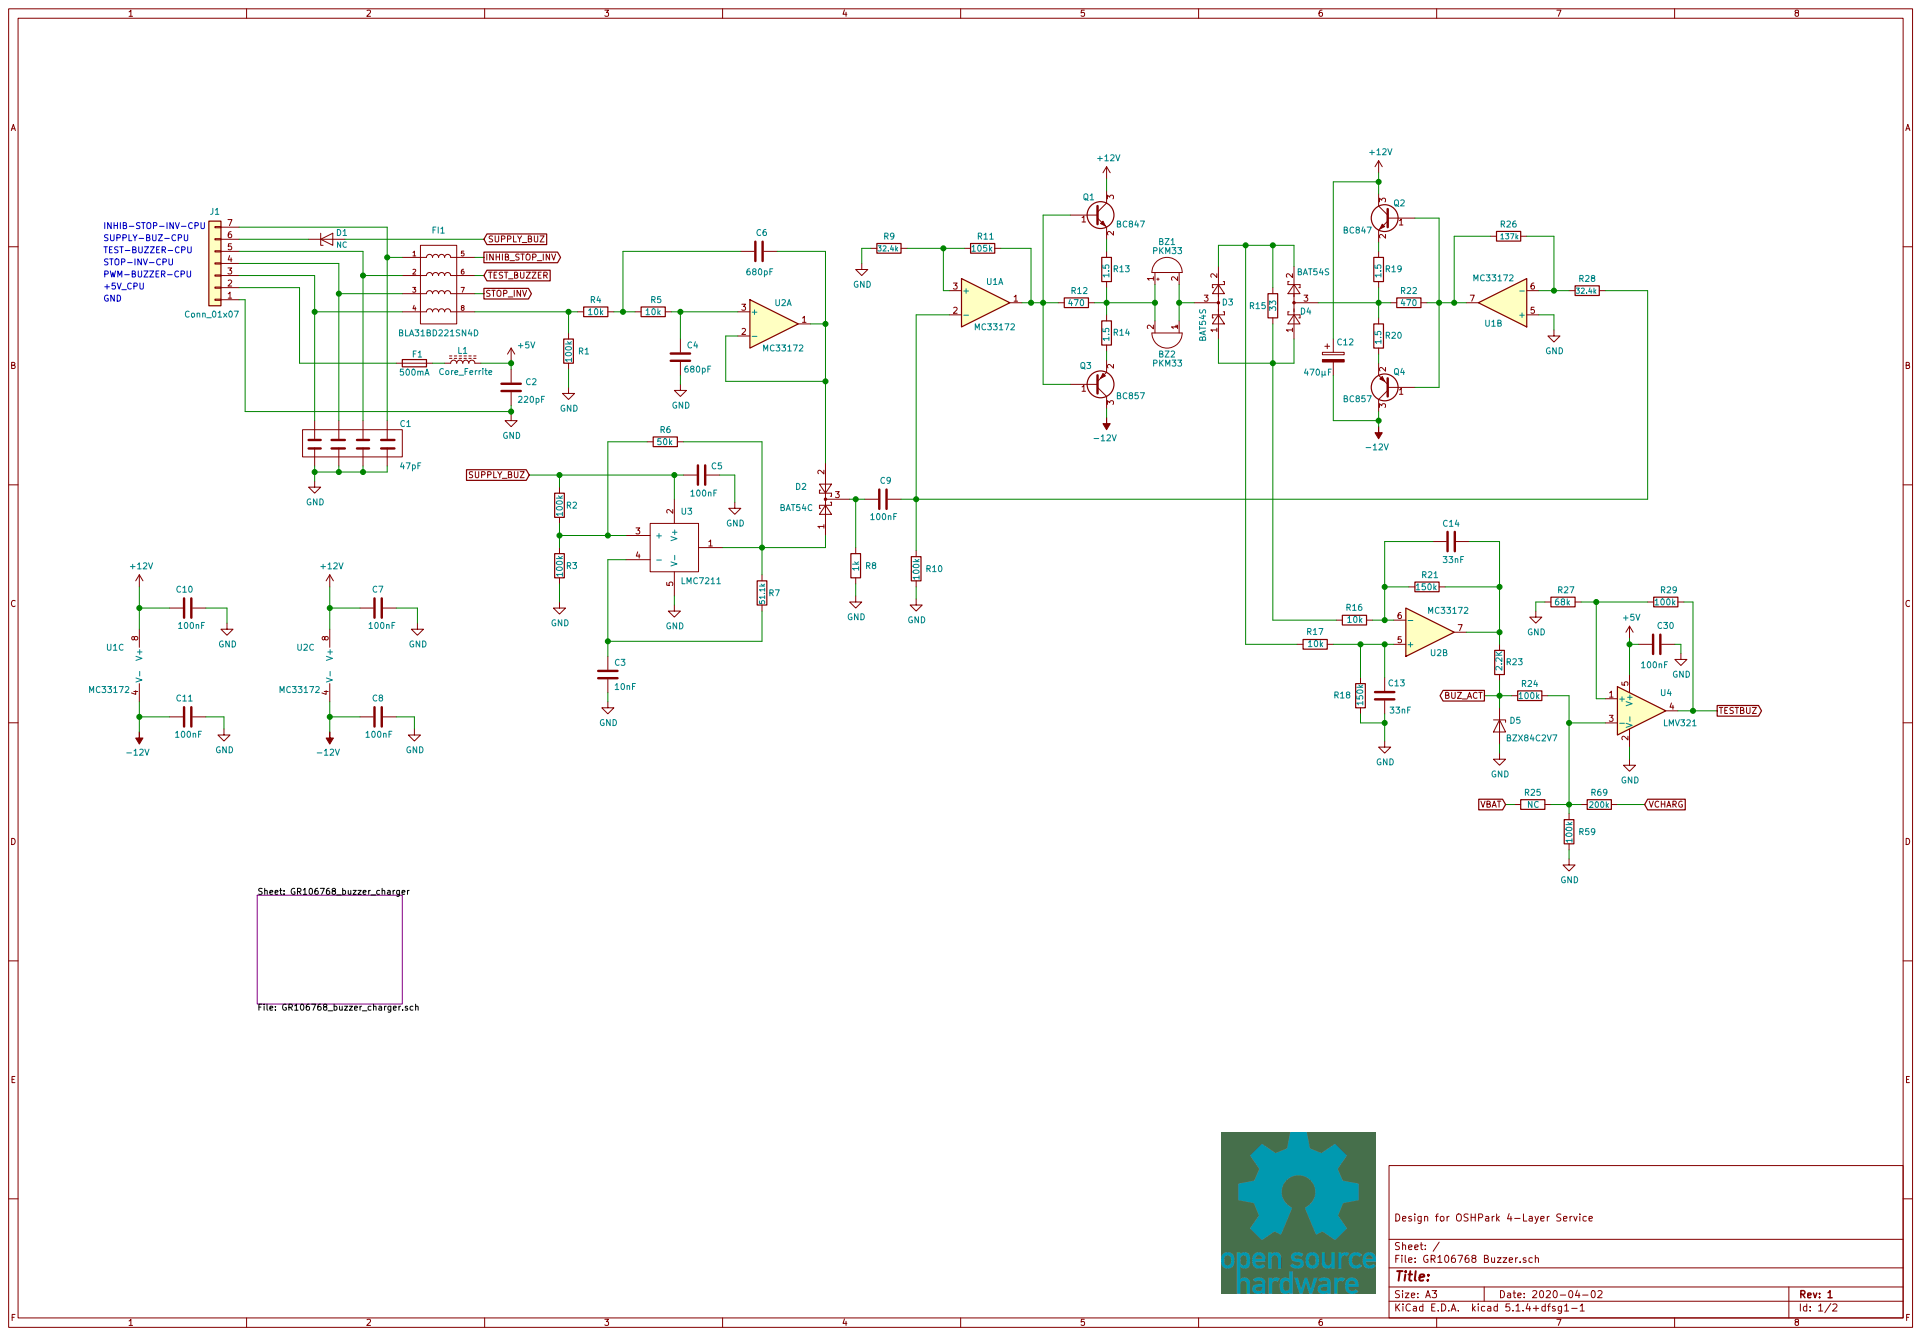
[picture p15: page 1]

INHIB-STOP-INV-CPU
SUPPLY-BUZ-CPU
TEST-BUZZER-CPU
STOP-INV-CPU GND
PWM-BUZZER-CPU
+5V_CPU

Id: 1/2 Title: File: GR106768 Buzzer.sch Sheet: / Design for OSHPark 4-Layer Service

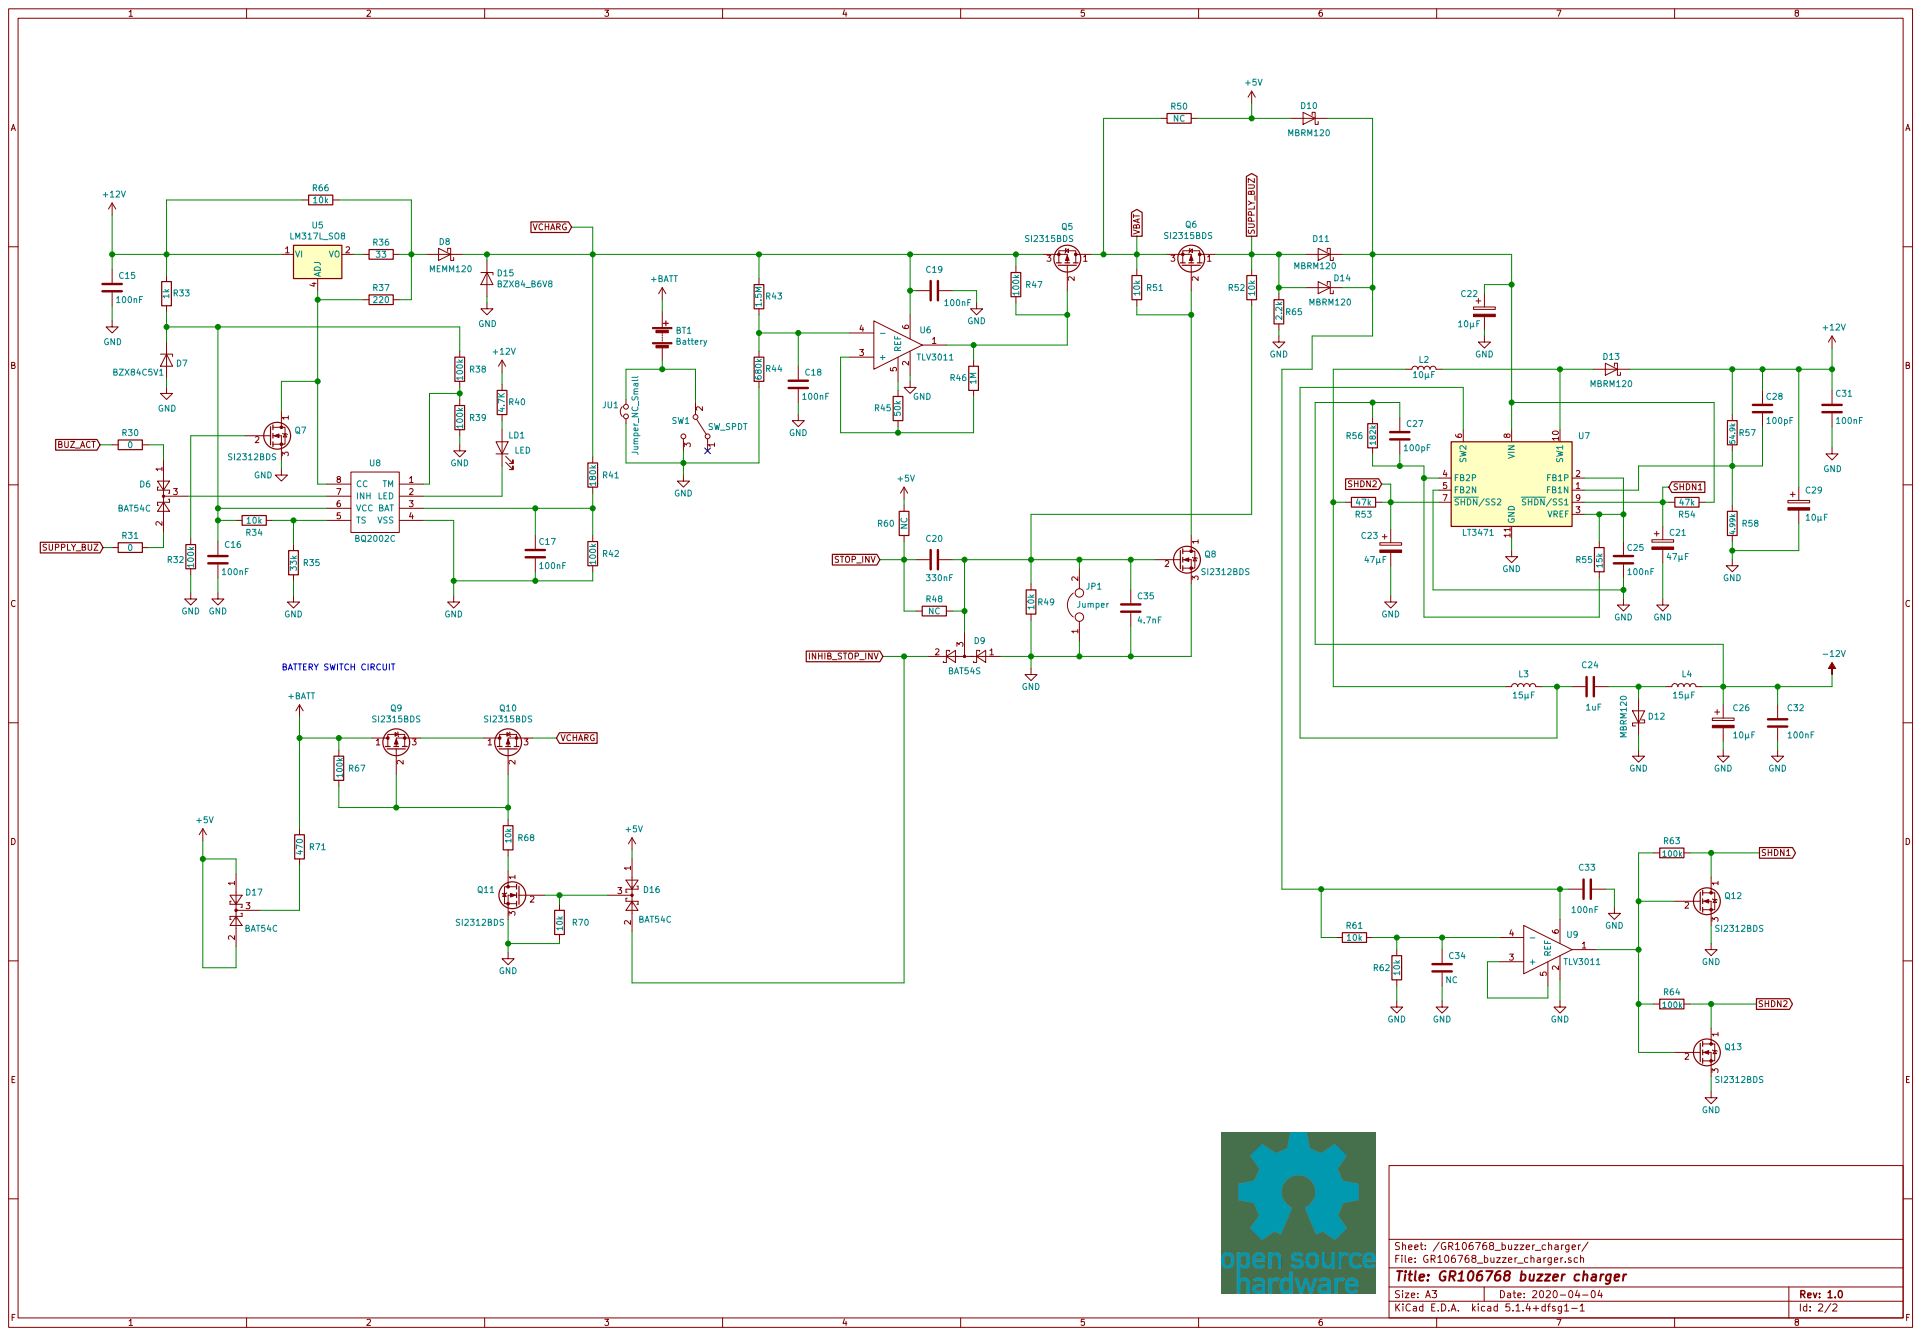
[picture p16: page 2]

Sheet: /GR106768_buzzer_charger/
File: GR106768_buzzer_charger.sch
Id: 2/2 Title: GR106768 buzzer charger

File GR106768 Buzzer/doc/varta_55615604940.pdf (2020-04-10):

This is controlled document.

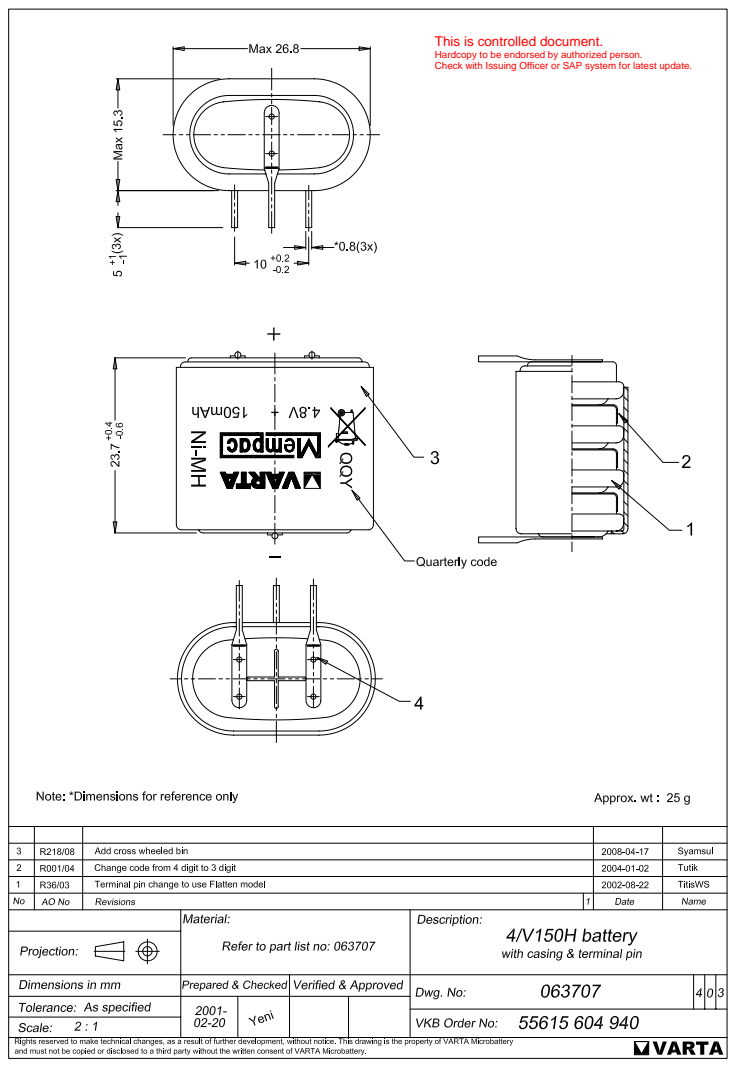
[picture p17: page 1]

Hardcopy to be endorsed by authorized person.
Check with Issuing Officer or SAP system for latest update.

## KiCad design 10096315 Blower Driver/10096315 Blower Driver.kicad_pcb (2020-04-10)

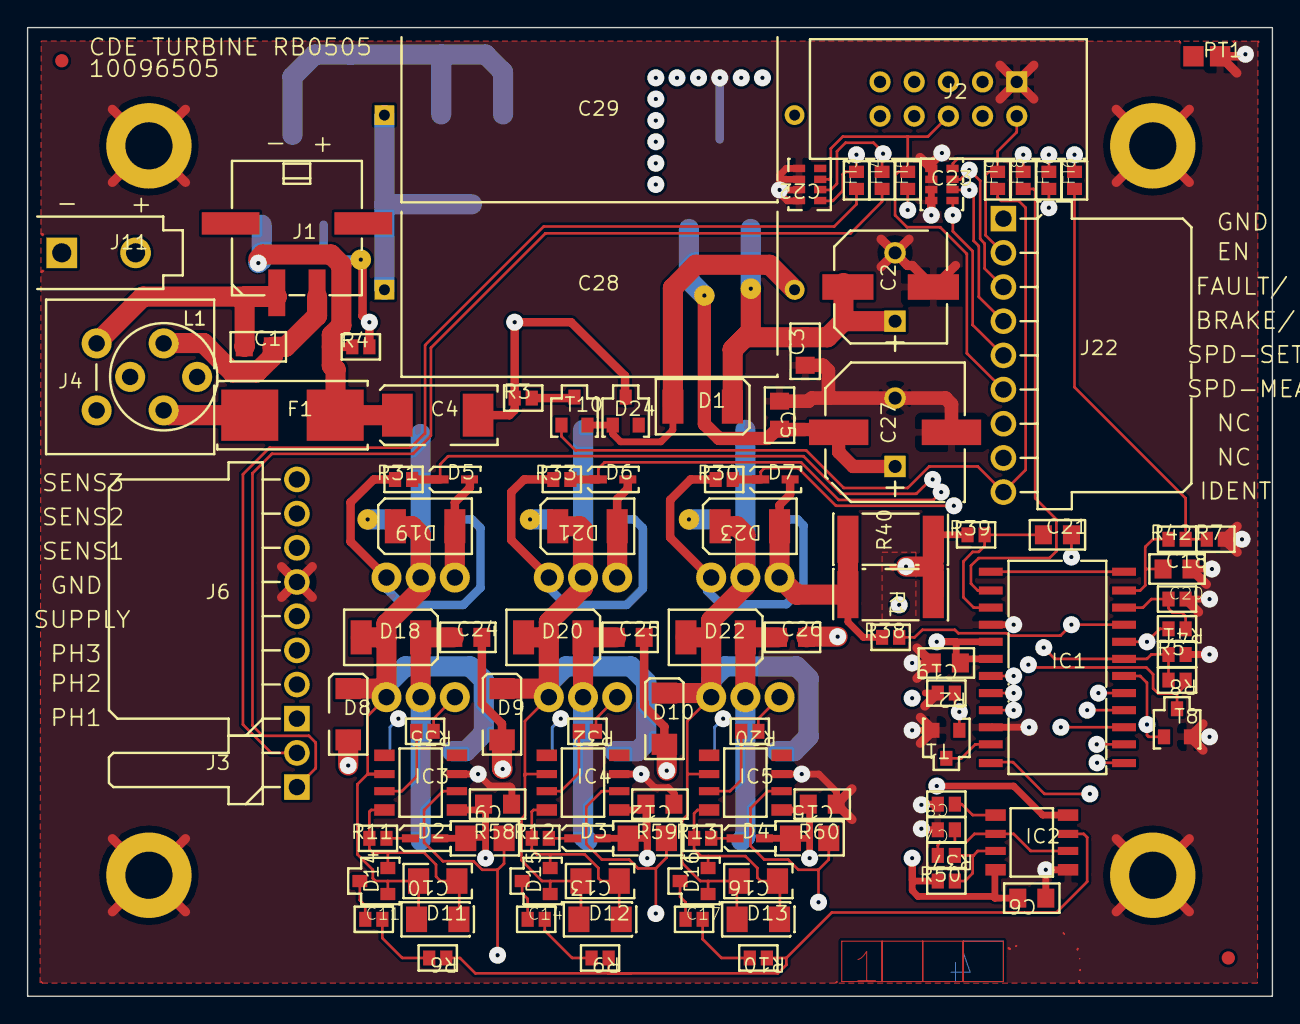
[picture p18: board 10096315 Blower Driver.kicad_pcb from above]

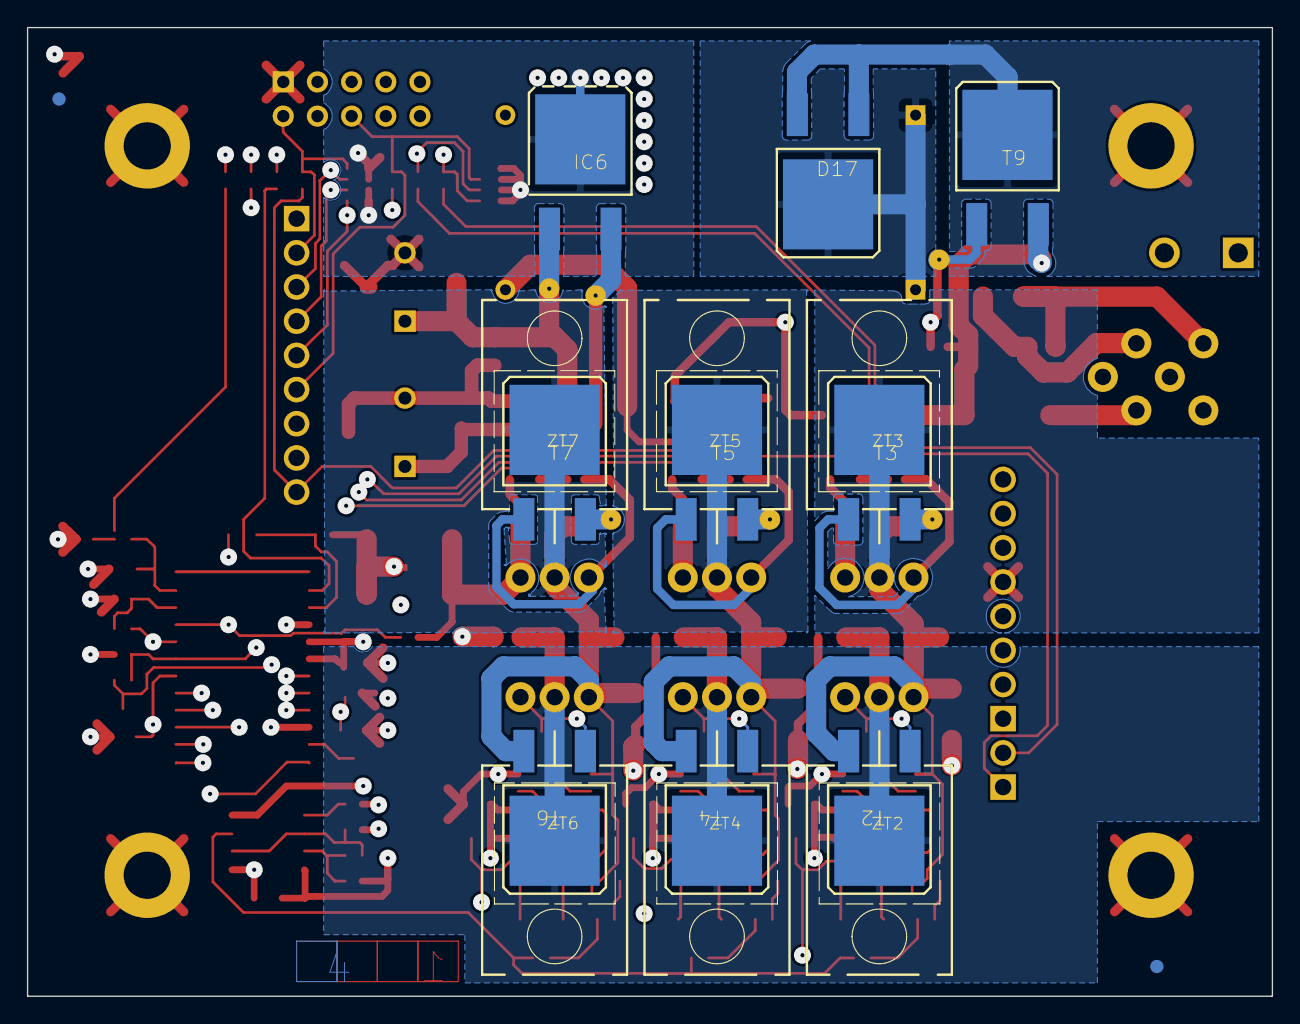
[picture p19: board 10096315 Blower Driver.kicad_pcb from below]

Board: 4 copper layers, 92.5 x 72.0 mm, 136 parts (18 on the bottom side), 67 nets.

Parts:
C1, C3, C5, C6, C9, C12, C15, C19, C21, C24, C25, C26: Capacitor_100nF; C0805
C2: Capacitor_100uF_CheckFootprint; 03515
C4: Capacitor_22uF_CheckFootprint; C7343
C7, C11, C14, C17: Capacitor_2.2nF; C0603
C8, C20: Capacitor_10nF; C0603
C10, C13, C16: Capacitor_220nF; RC1206
C18: Capacitor_330nF; C0805
C22, C23: CapacitorArray_47pf; C0612-4
C27: Capacitor_470uF_CheckFootprint; 03515
C28, C29: Capacitor_1000uF; HT-13X27
CAM5: FILM18_HORIZONTAL; FILM18_HORIZONTAL_1
CAM14, CAM15: FEE_COMP; FEE_COMP_1
D1, D18, D19, D20, D21, D22, D23: DiodeZener_30V; SMB
D2, D3, D4, D5, D6, D7: DiodeSchottky; SOD323
D8, D9, D10: DiodeZener_200V; SMA
D11, D12, D13: DiodeZener_30V; SOD80
D14, D15, D16, D24: DiodeSchottkySeriesPair; SOT23-1G
D17: DiodeSchottkyParallelPair; DPAK-2ANODES
F1: Fuse_5A; FU154000
FI1: FilterBNX002011; BNX002
FI3, FI4, FI5, FI6, FI7, FI8, FI9: FerriteBead; C0603
IC1: MotorDriver; MX.A24_COMPOSANT
IC2: NE555D; MX.A8_COMPOSANT
IC3, IC4, IC5: HighSideDriver; MX.A8_COMPOSANT
IC6: LinearRegulator; DPAK
J1: 2pinConnector_Power; MOL43650-02C
J2: 10pinConnector; BP2X5D
J3: 2pinConnector; MOL7395-2
J4: JumperBypass; JUMPER2_NoCopper
J6: 8pinConnector; MOL7395-8
J11: 2pinConnector_Unknown; MOL5566-2
J22: 9pinConnector; MOL7395-9
L1: Inductor_22uH; ELC09DxxxxF_NoCopper
MIR1, MIR2, MIR3, MIR4: Fiducial; MIRECMS-SAFT
NT1: Net-Tie_2; NetTie-2_SMD_Pad0.5mm
PT1: TestPoint; C12000
R1: Resistor_0R047; R2512
R2, R5, R37, R42: Resistor_10k; R0603
R3, R4, R7: Resistor_100k; R0603
R6, R9, R10: Resistor_680R; R0603
R8: Resistor_4k7; R0603
R11, R12, R13: Resistor_100R; R0603
R20, R30, R31, R32, R33, R35: Resistor_10R; R0603
R38, R39, R50: Resistor_1k; R0603
R40: Resistor_0R100; R2512
R41: Resistor_22k; R0603
R58, R59, R60: Resistor_1k_0.5W; RC1206
T1, T8, T10: MOSFET_NMOS_30V; SOT23-GSD
T2, T3, T4, T5, T6, T7: MOSFET_NMOS_55V; DPAK-GDS
T9: MOSFET_PMOS_60V; DPAK-GDS
ZC2: C-BCP-WX8; C-SC8_1
ZC27: C-BCP-WX10; C-SC10_1
ZM1, ZM2, ZM3, ZM4: MountingHole_Pad; FIX35M
ZT2, ZT3, ZT4, ZT5, ZT6, ZT7: Q-BT-TO220AB-GDS-INV; TO220ABGDS-INV_COUCHE

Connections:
+15V: C5.2, C6.2, C9.2, C12.2, C15.2, C19.1, C27.+, IC1.17, IC1.18, IC2.4, IC2.8, IC3.1, IC4.1, IC5.1, IC6.3, R50.2, R58.2, R59.2, R60.2, ZC27.+
+24V: C2.+, C3.2, C24.1, C25.1, C26.1, C28.+, C29.+, D1.2, D17.K, D18.2, D20.2, D22.2, IC6.1, T2.D, T4.D, T6.D, ZC2.+, ZT2.D, ZT4.D, ZT6.D
/BOT-DR-A: IC1.21, R30.1
/BOT-DR-B: IC1.20, R33.1
/BOT-DR-C: IC1.19, R31.1
/ISENS: D19.1, D21.1, D23.1, R1.1, R38.2, R40.2, T3.S, T5.S, T7.S, ZT3.S, ZT5.S, ZT7.S
/OE: FI9.2, IC1.7, J22.9, R5.2, R8.1, T10.G
/OSC: IC2.3, R6.2, R9.2, R10.2
/PHA1: C16.1, D10.2, D13.1, D16.1, D22.1, D23.2, IC5.6, J6.1, T6.S, T7.D, ZT6.S, ZT7.D
/PHA2: C13.1, D9.2, D12.1, D15.1, D20.1, D21.2, IC4.6, J6.2, T4.S, T5.D, ZT4.S, ZT5.D
/PHA3: C10.1, D8.2, D11.1, D14.1, D18.1, D19.2, IC3.6, J6.3, T2.S, T3.D, ZT2.S, ZT3.D
/SENSOR1: IC1.4, J6.6
/SENSOR2: IC1.5, J6.7
/SENSOR3: IC1.6, J6.8, T8.G
/TEMP+: FI3.2, J3.2
/TEMP-: FI4.2, J3.1
/TOP-DR-A: IC1.2, IC5.2, R60.1
/TOP-DR-B: IC1.1, IC4.2, R59.1
/TOP-DR-C: IC1.24, IC3.2, R58.1
/V-REF-M: IC1.3, IC1.8, J6.4, R41.1
GND: C2.-, C3.1, C5.1, C6.1, C7.1, C8.1, C9.1, C12.1, C15.1, C18.2, C19.2, C20.1, C22.5, C22.6, C22.7, C22.8, C23.1, C23.2, C23.3, C23.4, C27.-, IC1.16, IC1.22, IC2.1, IC3.3, IC4.3, IC5.3, IC6.2, J2.1, J6.5, J22.1, NT1.1, PT1.1, R2.1, R5.1, R7.1, T1.S, T8.S, ZC2.-, ZC27.-, ZM1.1, ZM2.1, ZM3.1, ZM4.1
GNDPWR: C24.2, C25.2, C26.2, C28.-, C29.-, D1.1, D8.1, D9.1, D10.1, D24.1, FI1.CG1, FI1.CG2, FI1.CG3, J4.2, NT1.2, R1.2, R39.2, R40.1, T10.S
unnamed: C1.1, FI1.PSG, J1.1, J4.1, J11.1
unnamed: C1.2, FI1.B, J1.2, J11.2, L1.1
unnamed: C4.+, F1.2, R4.2, T9.S
unnamed: C4.-, D24.3, R3.2, R4.1, T9.G
unnamed: C7.2, IC2.2, IC2.6, R37.1
unnamed: C8.2, IC2.5
unnamed: C10.2, D11.2, D14.2, IC3.8, R11.2
unnamed: C11.1, R6.1
unnamed: C11.2, D14.3
unnamed: C13.2, D12.2, D15.2, IC4.8, R12.2
unnamed: C14.1, R9.1
unnamed: C14.2, D15.3
unnamed: C16.2, D13.2, D16.2, IC5.8, R13.2
unnamed: C17.1, R10.1
unnamed: C17.2, D16.3
unnamed: C18.1, IC1.11, R42.2
unnamed: C20.2, IC1.10, R41.2
unnamed: C21.1, IC1.15, R39.1
unnamed: C21.2, IC1.9, R38.1
unnamed: C22.1, FI3.1, J2.10
unnamed: C22.2, FI4.1, J2.9
unnamed: C22.3, FI5.1, J2.6, J22.6
unnamed: C23.5, FI6.1, J2.5, J22.5
unnamed: C23.6, FI7.1, J2.4, J22.4
unnamed: C23.7, FI8.1, J2.3, J22.3
unnamed: C23.8, FI9.1, J2.2, J22.2
unnamed: D17.A1, D17.A2, T9.D
unnamed: F1.1, FI1.CB, L1.2
unnamed: FI5.2, R8.2, T8.D
unnamed: FI6.2, R7.2, R42.1
unnamed: FI7.2, R2.2, T1.G
unnamed: FI8.2, IC1.14
unnamed: IC1.12, IC1.13
unnamed: IC1.23, T1.D
unnamed: IC2.7, R37.2, R50.1
unnamed: IC3.7, R35.1
unnamed: IC4.7, R32.1
unnamed: IC5.7, R20.1
unnamed: R3.1, T10.D
unnamed: R20.2, T6.G, ZT6.G
unnamed: R30.2, T7.G, ZT7.G
unnamed: R31.2, T3.G, ZT3.G
unnamed: R32.2, T4.G, ZT4.G
unnamed: R33.2, T5.G, ZT5.G
unnamed: R35.2, T2.G, ZT2.G

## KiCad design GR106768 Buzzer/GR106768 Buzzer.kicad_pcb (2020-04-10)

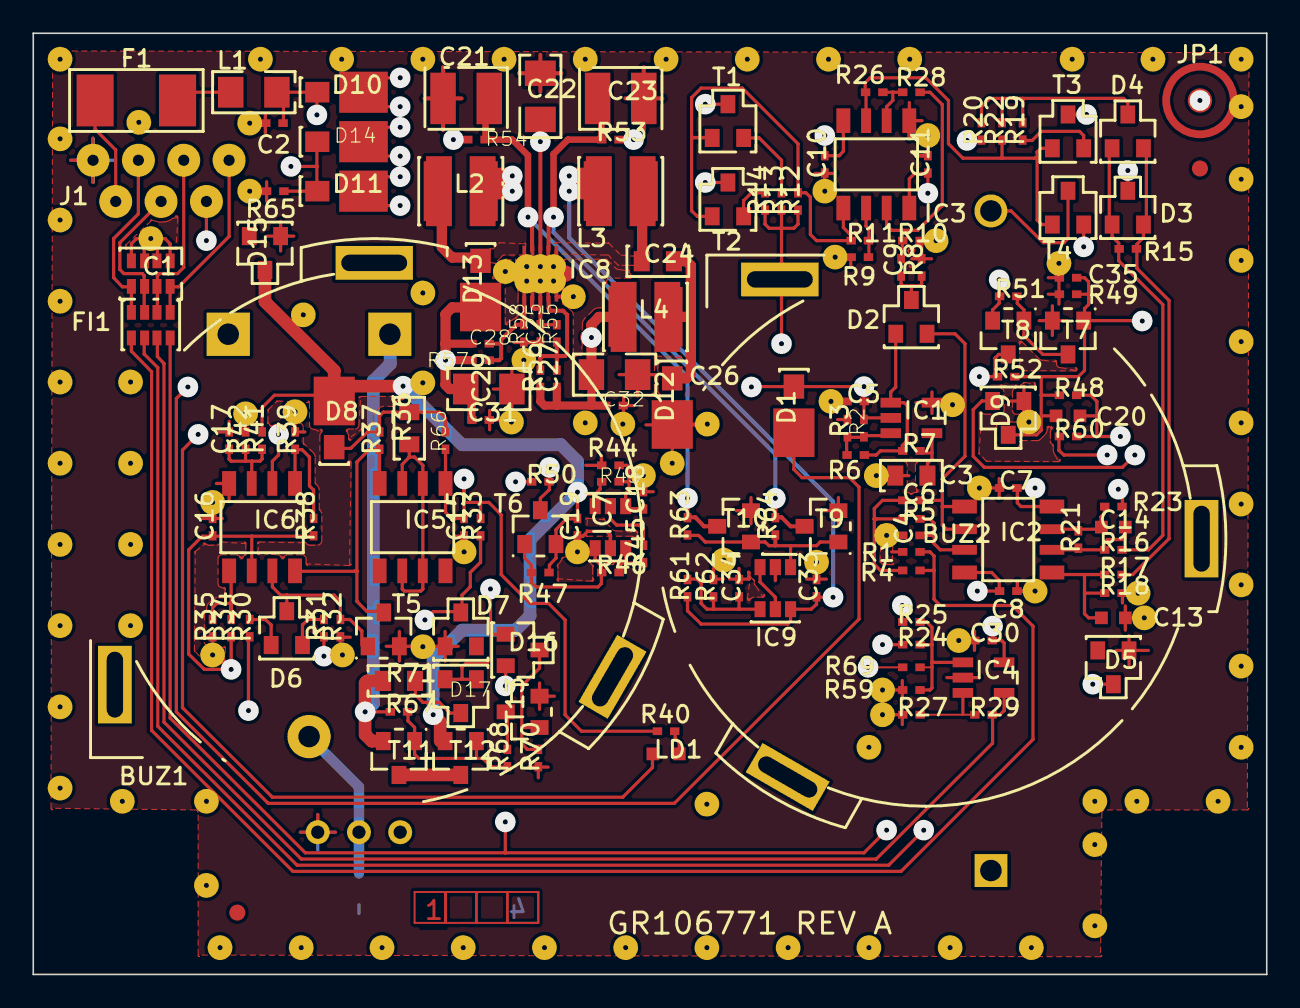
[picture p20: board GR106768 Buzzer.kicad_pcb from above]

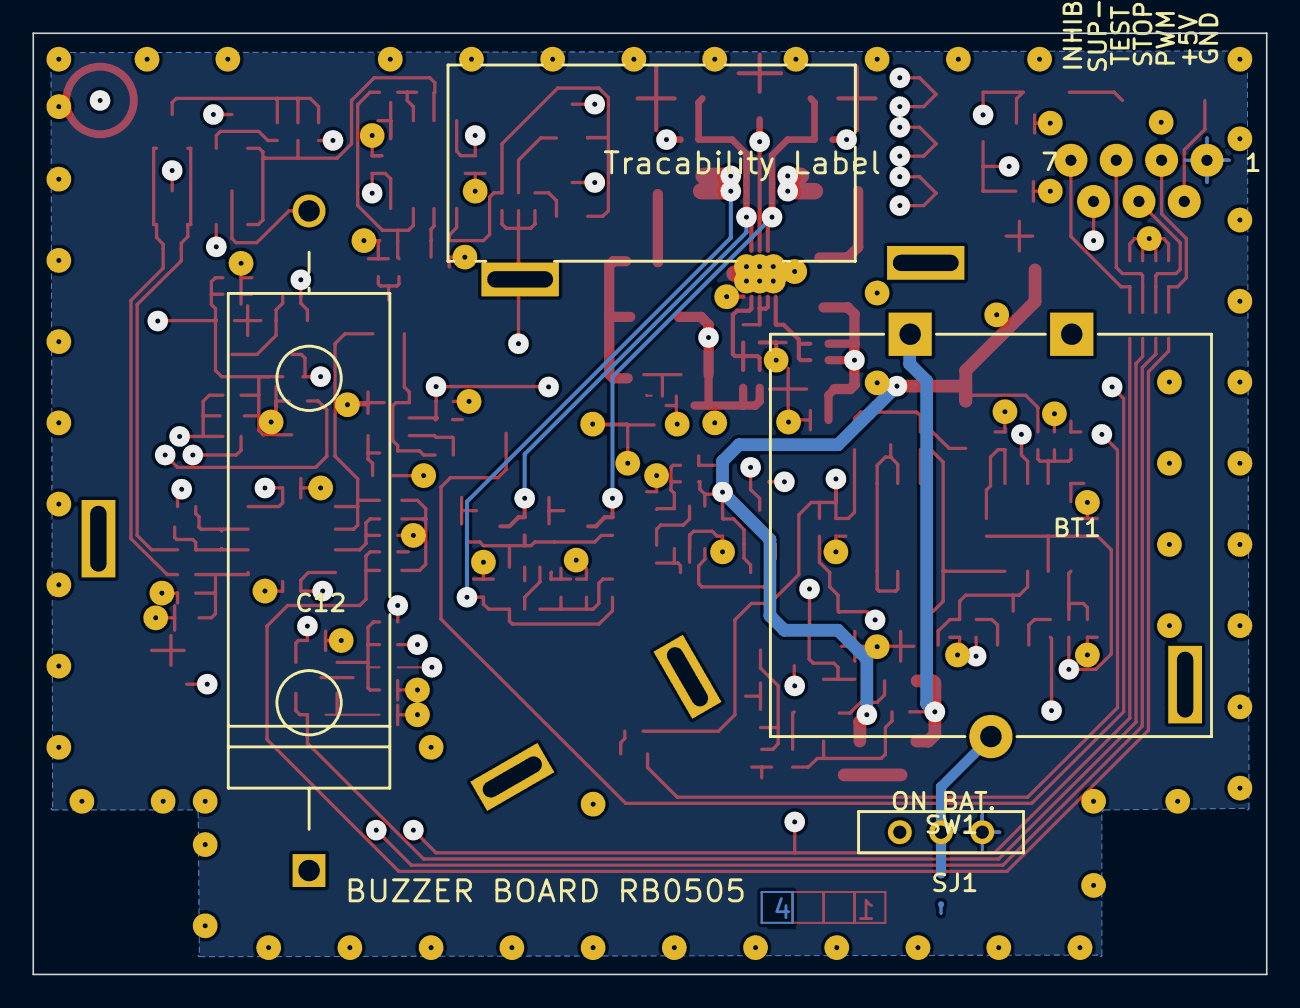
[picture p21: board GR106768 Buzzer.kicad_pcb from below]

Board: 4 copper layers, 76.0 x 58.0 mm, 168 parts (4 on the bottom side), 74 nets.

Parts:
BT1: Battery; BT-4-V150H-4.8V_1
BUZ1, BUZ2: PKM33; PKM33EPH-1201C_1
C1: 47pF; C0612-4_1
C2: 220pF; C0402_1
C3: 10nF; C0805_1
C4, C6: 680pF; C0402_2
C5, C7, C9, C10, C11, C15, C16, C17, C18, C19, C25, C30, C31, C32, C33: 100nF; C0402_2
C8: 100nF; C0402_1
C12: 470μF; AX10X30_1
C13: 33nF; C0603_1
C14: 33nF; C0603_2
C20: 330nF; C0603_1
C21, C23: 47μF; C1210_1
C22, C26, C29: 10μF; RC1206_1
C24: 1uF; C0805_1
C27, C28: 100pF; C0402_2
C34: NC; C0402_2
C35: 4.7nF; C0402_1
CAM1: A3_EQFC_COVIDIEN; A3_EQFC_COVIDIEN_1
CAM2: PER-COVIDIEN_TEXTE; PER-COVIDIEN_TEXTE_1
CAM3: A3_EQFS_COVIDIEN; A3_EQFS_COVIDIEN_1
CAM5: FILM13_HORIZONTAL; FILM13_HORIZONTAL_1
D1: NC; DO216AA_1
D2, D6, D16, D17: BAT54C; SOT23-1G_1
D3, D4, D9: BAT54S; SOT23-1G_1
D5: BZX84C2V7; SOT23-1G_1
D7: BZX84C5V1; SOT23-1G_1
D8: MEMM120; DO216AA_1
D10, D11, D12, D13, D14: MBRM120; DO216AA_1
D15: BZX84_B6V8; SOT23-1G_1
F1: 500mA; F6126_1
FI1: BLA31BD221SN4D; WE-FA_1
IC1: LMC7211; SOT23-5_1
IC2, IC3: MC33172; MX.A8_COMPOSANT_1
IC4: LMV321; SOT23-5_1
IC5: LM317L_SO8; MX.A8_COMPOSANT_1
IC6: BQ2002C; MX.A8_COMPOSANT_1
IC7: TLV3011; SOT23-6_1
IC8: LT3471; DFN10_1
IC9: TLV3011; SOT23-6_2
J1: Conn_01x07; BAR7-3-2-COVIDIEN_1
J2, J3: MIRECMS; MIRECMS-SAFT_1
JP1: Jumper; TB-CMS-AIROX_1
L1: Core_Ferrite; RC1206_1
L2: 10μH; WETPC-S_1
L2-2: SF-BC-NR4018; NR4018_1
L3, L4: 15μH; WETPC-S_1
L3-2, L4-2: SF-BC-NR4012; NR4012_1
LD1: LED; D0603_1
R1, R2, R3, R10, R24, R29, R32, R38, R39, R42, R47, R59, R63, R64, R67: 100k; R0402_1
R4, R5, R16, R17, R34, R49, R51, R52, R61, R62, R66, R68, R70: 10k; R0402_1
R6, R45: 50k; R0402_1
R7: 51.1k; R0402_1
R8, R33: 1k; R0402_1
R9, R28: 32.4k; R0402_1
R11: 105k; R0402_1
R12, R22: 470; R0402_1
R13, R14, R19, R20: 1.5; R0402_1
R15: 33; R0402_1
R18, R21: 150k; R0402_1
R23: 2.2K; R0402_1
R25, R48, R50, R60: NC; R0402_1
R26: 137k; R0402_1
R27: 68k; R0402_1
R30, R31: 0; R0402_1
R35: 33k; R0402_1
R36: 33; R0805_1
R37: 220; R0402_1
R40: 4.7K; R0402_1
R41: 180k; R0402_1
R43: 1.5M; R0402_1
R44: 680k; R0402_1
R46: 1M; R0402_1
R53, R54: 47k; R0402_1
R55: 15k; R0402_1
R56: 182k; R0402_1
R57: 54.9k; R0402_1
R58: 4.99k; R0402_1
R65: 2.2k; R0402_1
R69: 200k; R0402_1
R71: 470; R0805_1
SJ1: Jumper_NC_Small; TB-CMS-AIROX-2_1
SW1: SW_SPDT; NK236_1_1
T1, T3: BC847; SOT23-BEC_1
T2, T4: BC857; SOT23-BEC_1
T5, T7, T9, T10, T13: SI2312BDS; SOT23-GSD_1
T6, T8, T11, T12: SI2315BDS; SOT23-GSD_1

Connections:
+5V: C2.1, C30.1, D16.1, D17.1, D17.2, IC4.5, L1.2, R50.1, R60.1
+12V: C7.1, C10.1, C15.1, C28.1, C29.1, C31.1, IC2.8, IC3.8, IC5.1, R33.2, R40.2, R57.1, R66.2
+BATT: R67.1, R71.1
-12V: C8.1, C11.1, C26.1, C32.1, IC2.4, IC3.4, L4.2
/BUZ_ACT: D5.1, R23.1, R24.2, R30.2
/GR106768_buzzer_charger/SHDN1: C21.1, IC8.9, R54.2, R63.1
/GR106768_buzzer_charger/SHDN2: C23.1, IC8.7, R53.1, R64.1
/INHIB_STOP_INV: D9.2, D16.2
/STOP_INV: C20.2, R48.2, R60.2
/SUPPLY_BUZ: C5.2, IC1.2, R2.1, R31.2, R52.1, R65.1
/TEST_BUZZER: IC4.4, R29.1
/VBAT: R25.2, R50.2, R51.1
/VCHARG: C19.2, D15.1, IC7.6, R41.1, R43.2, R47.1, R69.1
GND: C1.5, C1.6, C1.7, C1.8, C2.2, C3.2, C4.2, C5.1, C7.2, C8.2, C10.2, C11.2, C13.1, C15.2, C16.2, C17.2, C18.2, C19.1, C21.2, C22.2, C23.2, C25.2, C26.2, C29.2, C30.2, C31.2, C32.2, C33.2, C34.2, C35.2, D5.2, D7.2, D9.1, D15.2, IC1.5, IC3.5, IC4.2, IC6.4, IC7.2, IC8.5, IC8.11, IC9.2, J1.1, R1.2, R3.2, R8.2, R9.2, R10.2, R18.1, R27.2, R32.2, R35.2, R39.2, R42.2, R44.1, R49.2, R58.2, R59.2, R62.2, R65.2, R70.2, SJ1.1, SW1.3
unnamed: SJ1.2, SW1.2
unnamed: BUZ1.1, BUZ2.2, R12.1, R13.1, R14.2
unnamed: BUZ1.2, BUZ2.1, D3.3
unnamed: C1.1, J1.3
unnamed: C1.2, J1.4
unnamed: C1.3, J1.5
unnamed: C1.4, J1.7
unnamed: C3.1, IC1.4, R7.2
unnamed: C4.1, IC2.3, R5.1
unnamed: C6.1, R4.1, R5.2
unnamed: C6.2, D2.2, IC2.1, IC2.2
unnamed: C9.1, D2.3, R8.1
unnamed: C9.2, IC3.2, R10.1, R28.1
unnamed: C13.2, IC2.5, R17.2, R18.2
unnamed: C14.1, IC2.7, R21.1, R23.2
unnamed: C14.2, IC2.6, R16.2, R21.2
unnamed: C16.1, D7.1, IC6.6, R33.1, R34.2, R38.1
unnamed: C17.1, IC6.3, R41.2, R42.1
unnamed: C18.1, IC7.4, R43.1, R44.2
unnamed: C20.1, C35.1, D9.3, JP1.2, R48.1, R49.1, R52.2
unnamed: C22.1, C33.1, IC8.8, IC9.6, R54.1, R61.2
unnamed: C24.1, IC8.6, L3.2
unnamed: C24.2, L4.1
unnamed: C25.1, IC8.2, IC8.3, R55.1
unnamed: C27.1, R56.1
unnamed: C27.2, IC8.4, R55.2, R56.2
unnamed: C28.2, IC8.1, R57.2, R58.1
unnamed: C34.1, IC9.4, R61.1, R62.1
unnamed: D2.1, IC1.1, R6.1, R7.1
unnamed: D3.1, D4.1, R15.2, R16.1
unnamed: D3.2, D4.2, R15.1, R17.1
unnamed: D4.3, R19.1, R20.2, R22.2
unnamed: D6.1, R30.1
unnamed: D6.2, R31.1
unnamed: D6.3, IC6.7
unnamed: R36.1, R37.1, R66.1
unnamed: IC8.10, L2.2
unnamed: D16.3, R70.1
unnamed: D17.3, R71.2
unnamed: F1.1, L1.1
unnamed: F1.2, J1.2
unnamed: R1.1, R4.2
unnamed: IC1.3, R2.2, R3.1, R6.2
unnamed: IC3.1, R11.1, R12.2
unnamed: IC3.3, R9.1, R11.2
unnamed: IC3.6, R26.1, R28.2
unnamed: IC3.7, R22.1, R26.2
unnamed: IC4.1, R24.1, R25.1, R59.1, R69.2
unnamed: IC4.3, R27.1, R29.2
unnamed: IC5.2, IC5.3, IC5.6, IC5.7, R36.2
unnamed: IC5.4, IC6.8, R37.2
unnamed: IC6.1, R38.2, R39.1
unnamed: IC6.5, R34.1, R35.1
unnamed: IC7.1, R46.2, R47.2
unnamed: IC7.3, R45.1, R46.1
unnamed: IC7.5, R45.2
unnamed: IC9.1, R63.2, R64.2
unnamed: IC9.3, IC9.5
unnamed: L2.1, L3.1, R53.2
unnamed: R67.2, R68.1

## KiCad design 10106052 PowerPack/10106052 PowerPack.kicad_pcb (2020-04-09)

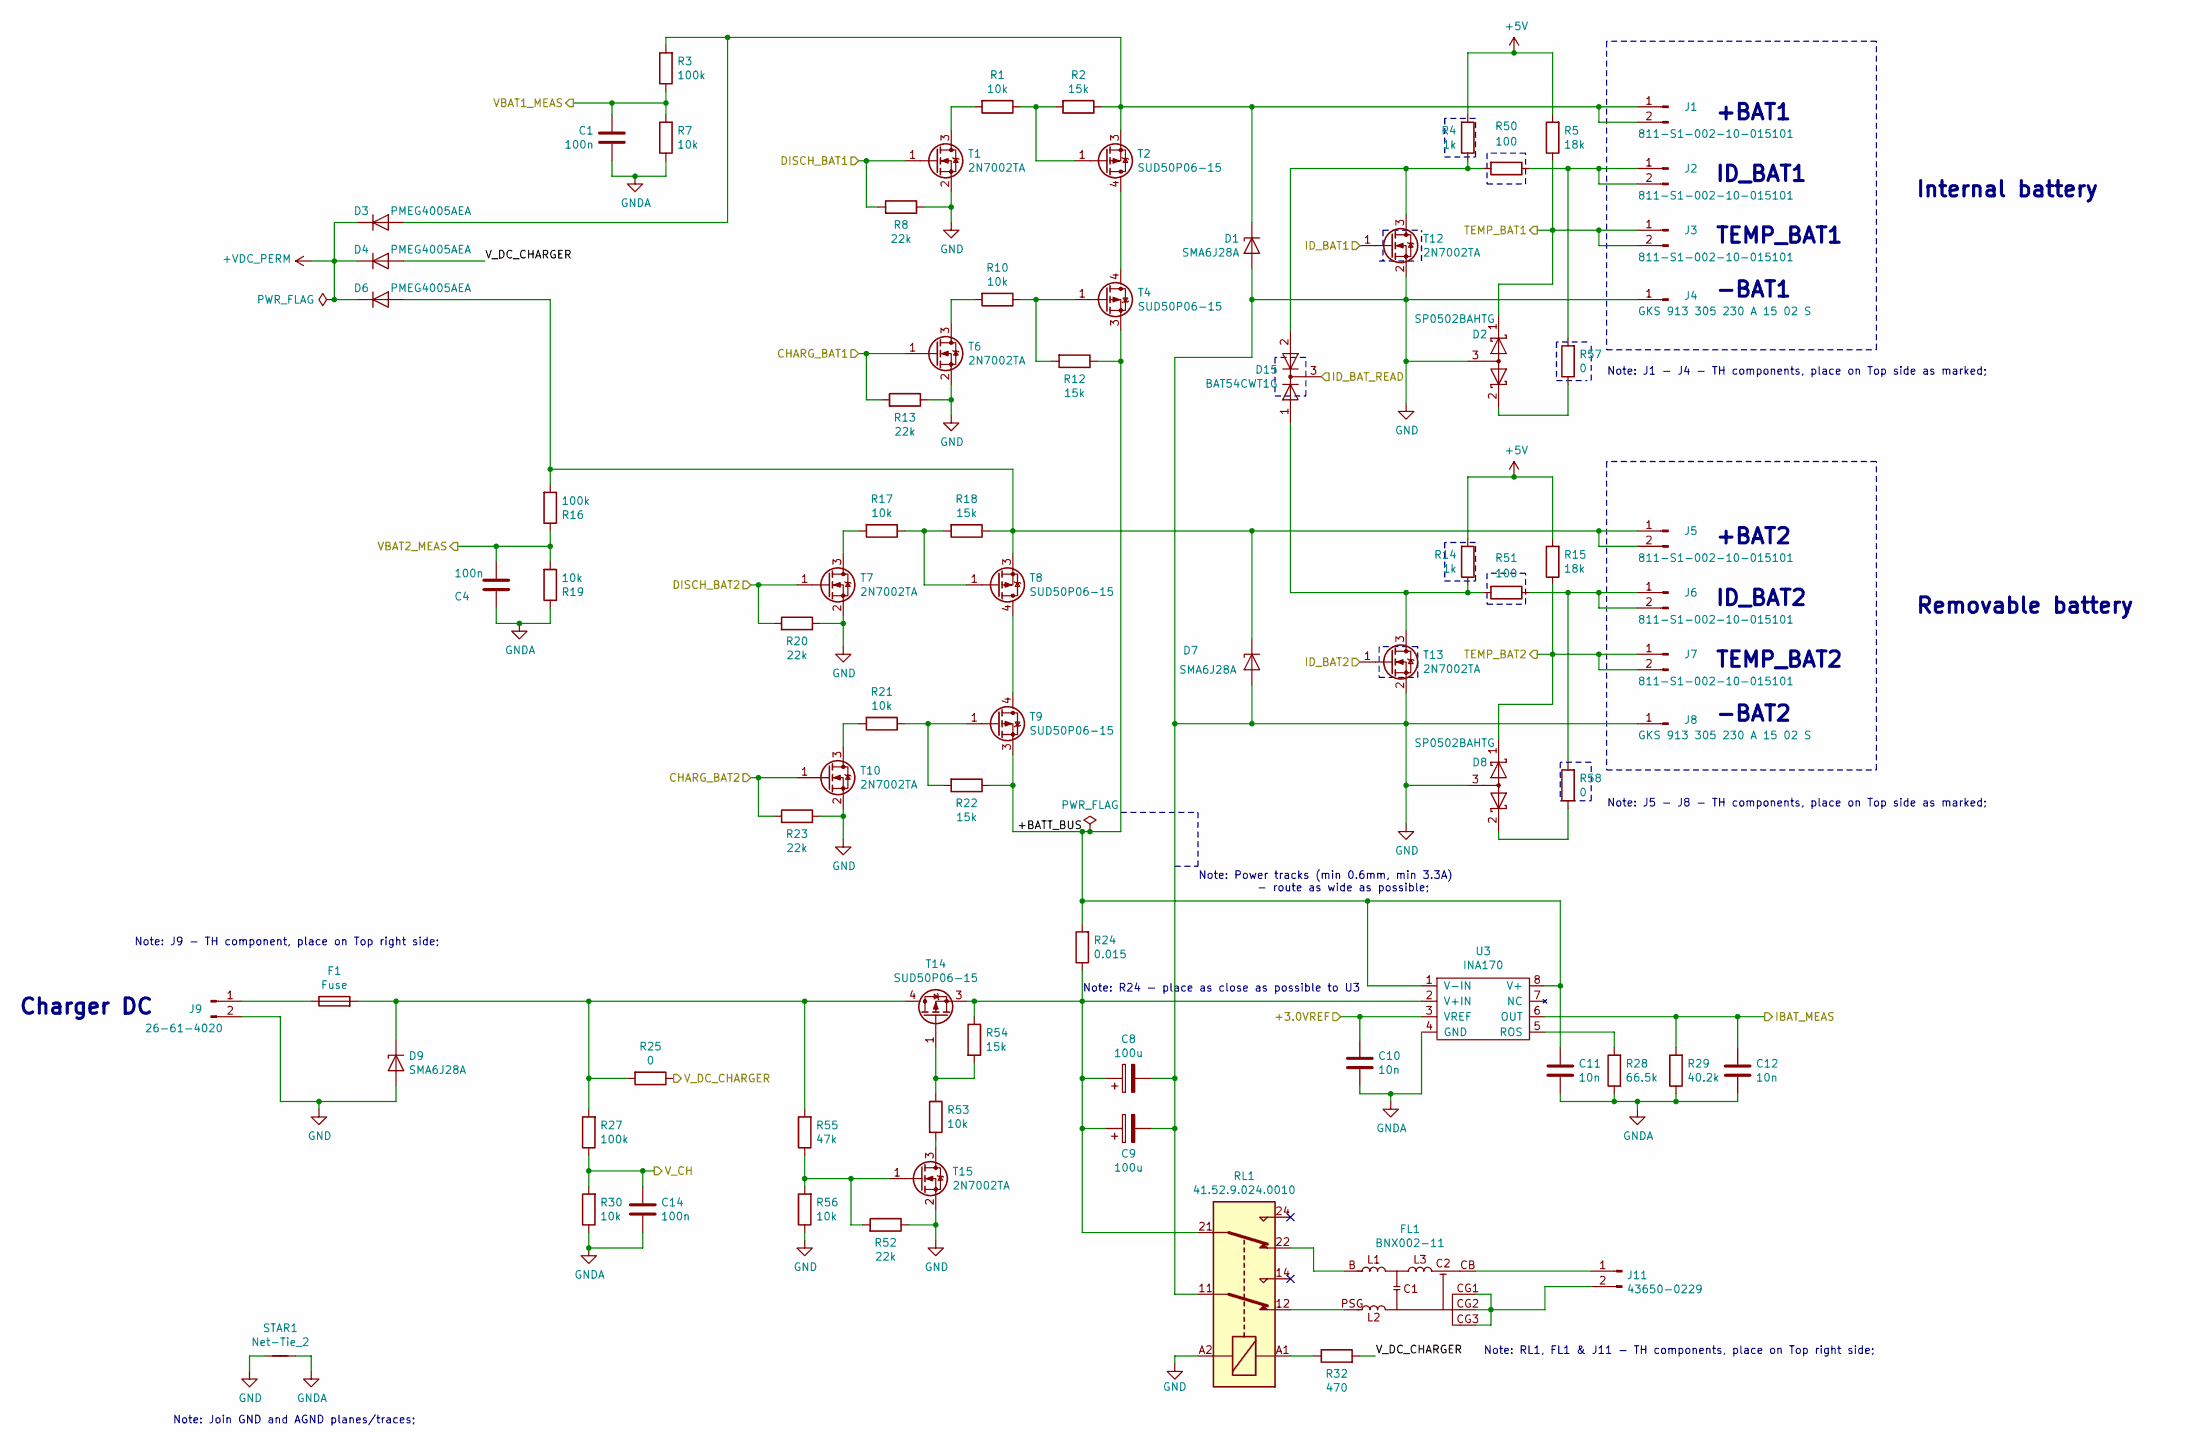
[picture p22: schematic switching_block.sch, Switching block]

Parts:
C1, C4, C14: 100n; CAPC1608X86N
C8, C9: 100u; CAPPRD350W60D800H1250PBA
C10, C11, C12: 10n; CAPC1608X86N
D1, D7, D9: SMA6J28A; DIOM5126X203N_SWP
D2, D8: SP0502BAHTG; SOT65P220X110-3N
D3, D4, D6: PMEG4005AEA; SOD2512X110N_SWP
D15: BAT54CWT1G; SOT65P220X110-3N
F1: Fuse; FUS4755X155N
FL1: BNX002-11; BNX00201
J1, J2, J3, J5, J6, J7: 811-S1-002-10-015101; CON254W80L508T254H600P
J4, J8: GKS 913 305 230 A 15 02 S; GKS-913-305-230-A-15-02-S
J9: 26-61-4020; CON2PHDR1000W777L396P
J11: 43650-0229; CON-43650-0229
R1, R7, R10, R17, R19, R21, R30, R53, R56: 10k; RESC1608X50AN
R2, R12, R18, R22, R54: 15k; RESC1608X50AN
R3, R16, R27: 100k; RESC1608X50AN
R4, R14: 1k; RESC1608X50AN
R5, R15: 18k; RESC1608X50AN
R8, R13, R20, R23, R52: 22k; RESC1608X50AN
R24: 0.015; RESC6533X80N
R25: 0; RESC3216X60N
R28: 66.5k; RESC1608X50AN
R29: 40.2k; RESC1608X50AN
R32: 470; RESC3216X60N
R50, R51: 100; RESC1608X50AN
R55: 47k; RESC1608X50AN
R57, R58: 0; RESC1608X50AN
RL1: 41.52.9.024.0010; RLY-41-52-9-024-0010
STAR1: Net-Tie_2; STAR
T1, T6, T7, T10, T12, T13, T15: 2N7002TA; SOT92P240X120-3N
T2, T4, T8, T9, T14: SUD50P06-15; TO228P1003X238-3_4N
U3: INA170; SOP65P490X110-8N

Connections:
+3.0VREF: C10.2, U3.3 (VREF); also elsewhere on the board
+5V: R4.2, R5.2, R14.2, R15.2; also elsewhere on the board
+VDC_PERM: D3.2 (K), D4.2 (K), D6.2 (K); also elsewhere on the board
/CHARG_BAT1: R13.2, T6.1 (G); also elsewhere on the board
/CHARG_BAT2: R23.2, T10.1 (G); also elsewhere on the board
/DISCH_BAT1: R8.2, T1.1 (G); also elsewhere on the board
/DISCH_BAT2: R20.2, T7.1 (G); also elsewhere on the board
/IBAT_MEAS: C12.2, R29.2, U3.6 (OUT); also elsewhere on the board
/ID_BAT1: T12.1 (G); also elsewhere on the board
/ID_BAT2: T13.1 (G); also elsewhere on the board
/ID_BAT_READ: D15.3 (K); also elsewhere on the board
/Switching block/+BATT_BUS: C11.2, R12.1, R22.1, R24.2, T4.3 (S), T9.3 (S), U3.1 (V-IN), U3.8 (V+)
/TEMP_BAT1: D2.1 (K), J3.1, J3.2, R5.1; also elsewhere on the board
/TEMP_BAT2: D8.1 (K), J7.1, J7.2, R15.1; also elsewhere on the board
/VBAT1_MEAS: C1.2, R3.1, R7.2; also elsewhere on the board
/VBAT2_MEAS: C4.2, R16.1, R19.2; also elsewhere on the board
/V_CH: C14.2, R27.1, R30.2; also elsewhere on the board
/V_DC_CHARGER: D4.1 (A), R25.1, R32.2; also elsewhere on the board
GND: C8.2, C9.2, D1.1 (A), D2.3 (A), D7.1 (A), D8.3 (A), D9.1 (A), J4.1, J8.1, J9.2, R8.1, R13.1, R20.1, R23.1, R52.1, R56.1, RL1.11, RL1.A2, STAR1.1, T1.2 (S), T6.2 (S), T7.2 (S), T10.2 (S), T12.2 (S), T13.2 (S), T15.2 (S); also elsewhere on the board
GNDA: C1.1, C4.1, C10.1, C11.1, C12.1, C14.1, R7.1, R19.1, R28.1, R29.1, R30.1, STAR1.2, U3.4 (GND); also elsewhere on the board
unnamed: C8.1, C9.1, R24.1, R54.1, RL1.21, T14.3 (S), U3.2 (V+IN)
unnamed: D1.2 (K), D3.1 (A), J1.1, J1.2, R2.1, R3.2, T2.3 (S)
unnamed: D2.2 (K), R57.1
unnamed: D6.1 (A), D7.2 (K), J5.1, J5.2, R16.2, R18.1, T8.3 (S)
unnamed: D8.2 (K), R58.1
unnamed: D9.2 (K), F1.2, R25.2, R27.2, R55.2, T14.4 (D)
unnamed: D15.1 (A), R14.1, R51.2, T13.3 (D)
unnamed: D15.2 (A), R4.1, R50.2, T12.3 (D)
unnamed: F1.1, J9.1
unnamed: FL1.B, RL1.22
unnamed: FL1.CB, J11.1
unnamed: FL1.CG1, FL1.CG2, FL1.CG3, J11.2
unnamed: FL1.PSG, RL1.12
unnamed: J2.1, J2.2, R50.1, R57.2
unnamed: J6.1, J6.2, R51.1, R58.2
unnamed: R1.1, R2.2, T2.1 (G)
unnamed: R1.2, T1.3 (D)
unnamed: R10.1, R12.2, T4.1 (G)
unnamed: R10.2, T6.3 (D)
unnamed: R17.1, R18.2, T8.1 (G)
unnamed: R17.2, T7.3 (D)
unnamed: R21.1, R22.2, T9.1 (G)
unnamed: R21.2, T10.3 (D)
unnamed: R28.2, U3.5 (ROS)
unnamed: R32.1, RL1.A1
unnamed: R52.2, R55.1, R56.2, T15.1 (G)
unnamed: R53.1, R54.2, T14.1 (G)
unnamed: R53.2, T15.3 (D)
unnamed: T2.4 (D), T4.4 (D)
unnamed: T8.4 (D), T9.4 (D)

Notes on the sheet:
ID_BAT2
TEMP_BAT2
+BAT1
ID_BAT1
TEMP_BAT1
-BAT1
Internal battery
Removable battery
Note: J1 - J4 - TH components, place on Top side as marked;
Note: J5 - J8 - TH components, place on Top side as marked;
Note: Power tracks (min 0.6mm, min 3.3A) - route as wide as possible;
Note: RL1, FL1 & J11 - TH components, place on Top right side;
Charger DC
Note: J9 - TH component, place on Top right side;
Note: R24 - place as close as possible to U3
Note: Join GND and AGND planes/traces;
+BAT2
-BAT2

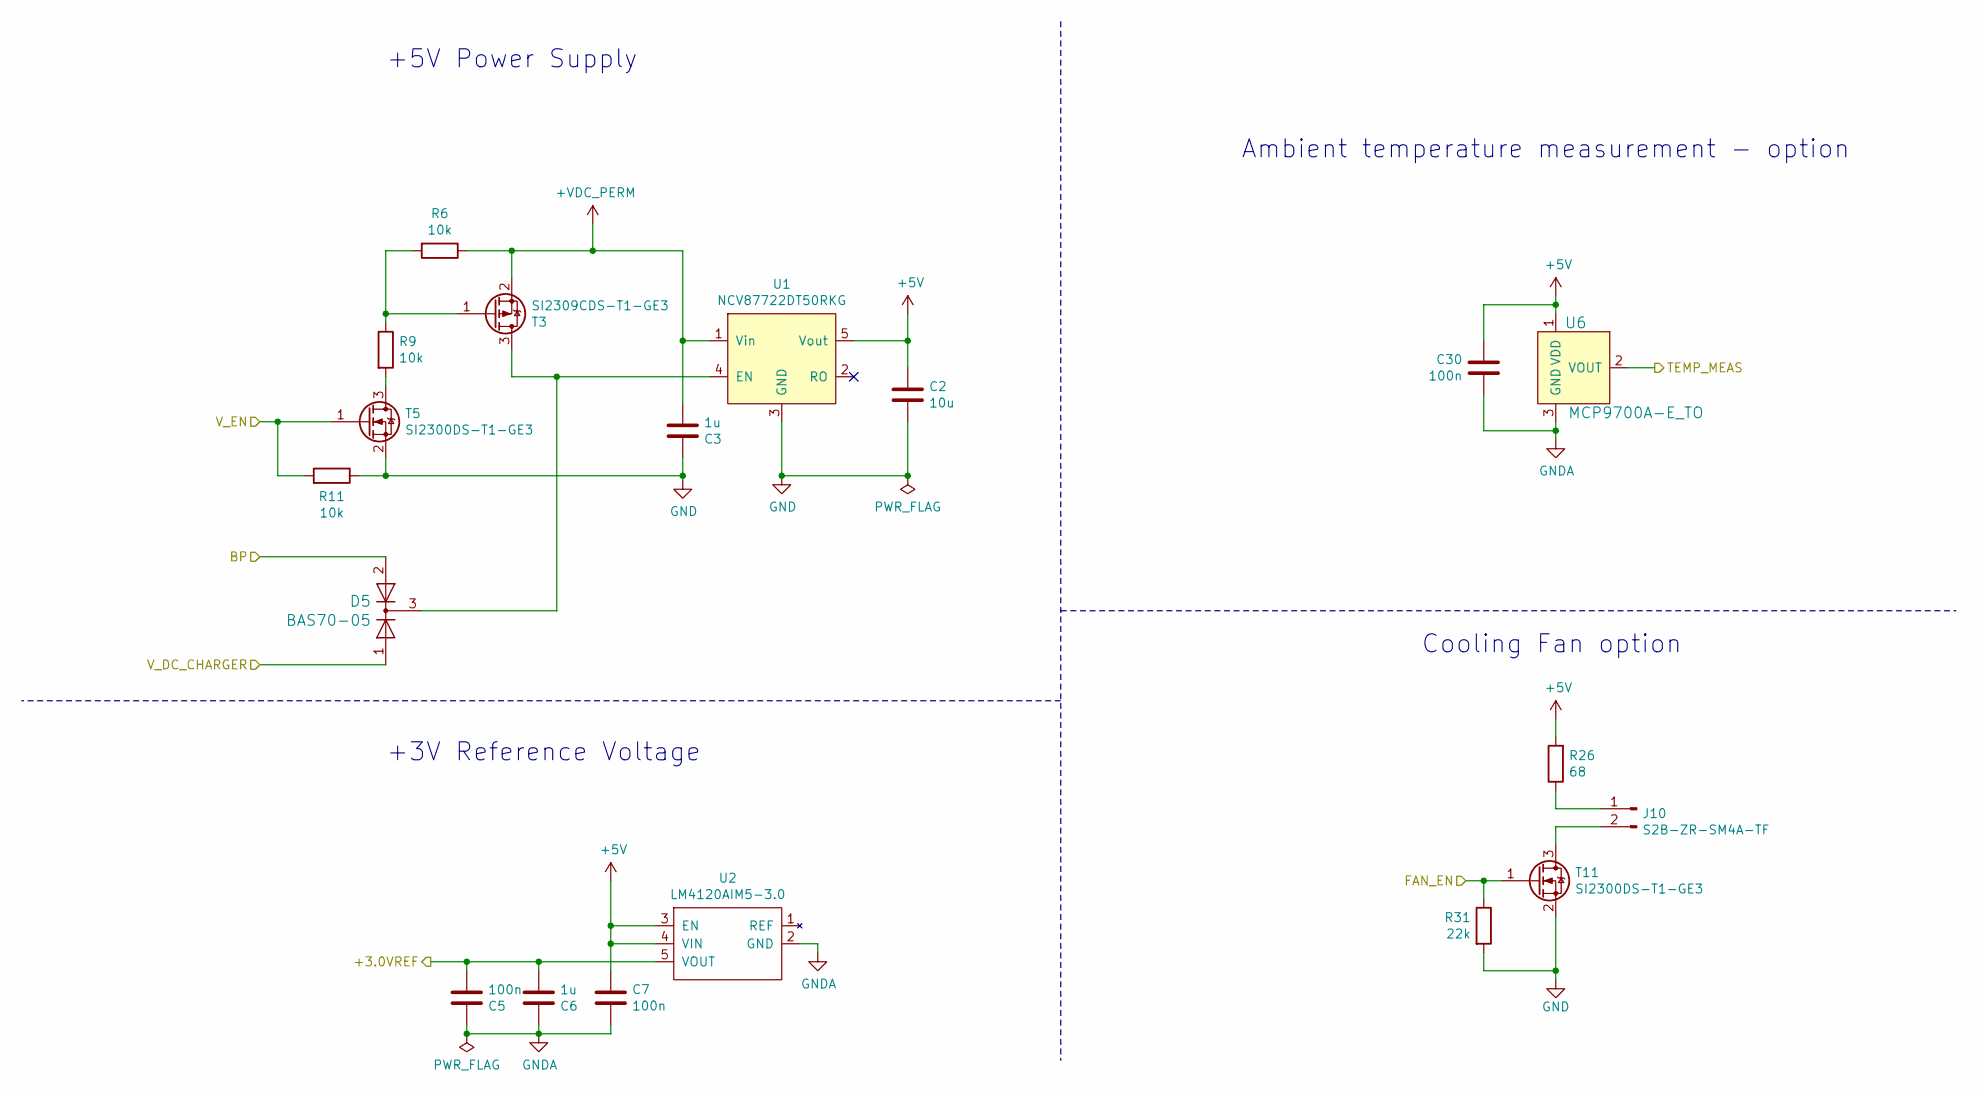
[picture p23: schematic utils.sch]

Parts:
C2: 10u; CAPC1608X86N
C3: 1u; CAPC3225X155N
C5, C7, C30: 100n; CAPC1608X86N
C6: 1u; CAPC1608X86N
D5: BAS70-05; SOT92P240X120-3N
J10: S2B-ZR-SM4A-TF; CON-S2B-ZR-SM4A-TF
R6, R9, R11: 10k; RESC1608X50AN
R26: 68; RESC3216X60N
R31: 22k; RESC1608X50AN
T3: SI2309CDS-T1-GE3; SOT92P240X120-3N
T5, T11: SI2300DS-T1-GE3; SOT92P240X120-3N
U1: NCV87722DT50RKG; TO170P1420X457-8NA
U2: LM4120AIM5-3.0; SOT95P279X142-5N
U6: MCP9700A-E_TO; TO-92; Digi-Key_PN MCP9700A-E/TO-ND

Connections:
+3.0VREF: C5.2, C6.2, U2.5 (VOUT); also elsewhere on the board
+5V: C2.2, C7.2, C30.2, R26.2, U1.5 (Vout), U2.3 (EN), U2.4 (VIN), U6.1 (VDD); also elsewhere on the board
+VDC_PERM: C3.2, R6.1, T3.2 (S), U1.1 (Vin); also elsewhere on the board
/BP: D5.2 (A); also elsewhere on the board
/FAN_EN: R31.1, T11.1 (G); also elsewhere on the board
/TEMP_MEAS: U6.2 (VOUT); also elsewhere on the board
/V_DC_CHARGER: D5.1 (A); also elsewhere on the board
/V_EN: R11.2, T5.1 (G); also elsewhere on the board
GND: C2.1, C3.1, R11.1, R31.2, T5.2 (S), T11.2 (S), U1.3 (GND); also elsewhere on the board
GNDA: C5.1, C6.1, C7.1, C30.1, U2.2 (GND), U6.3 (GND); also elsewhere on the board
unnamed: D5.3 (K), T3.3 (D), U1.4 (EN)
unnamed: J10.1, R26.1
unnamed: J10.2, T11.3 (D)
unnamed: R6.2, R9.1, T3.1 (G)
unnamed: R9.2, T5.3 (D)

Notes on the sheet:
Ambient temperature measurement - option
Cooling Fan option
+5V Power Supply
+3V Reference Voltage

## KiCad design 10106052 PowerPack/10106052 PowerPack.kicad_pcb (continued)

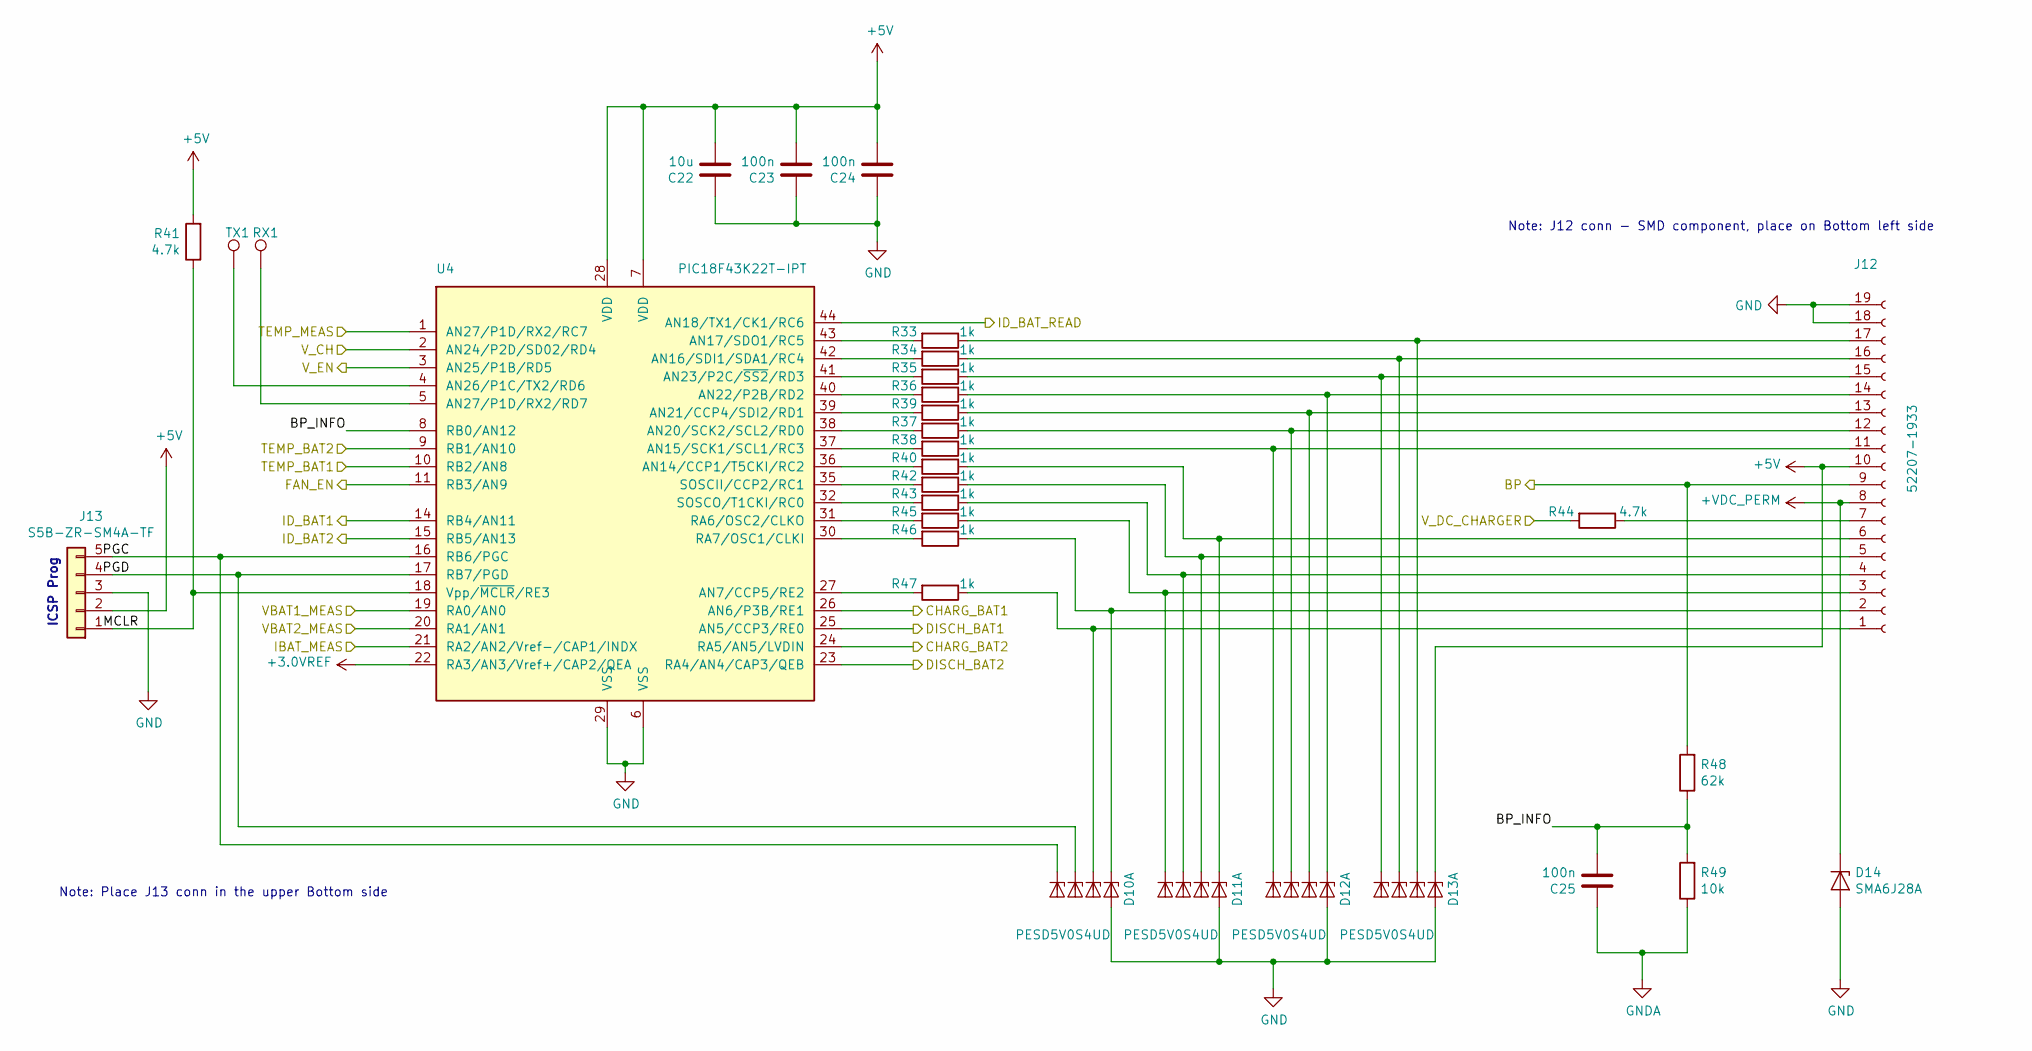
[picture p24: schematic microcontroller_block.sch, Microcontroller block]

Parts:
C22: 10u; CAPC1608X86N
C23, C24, C25: 100n; CAPC1608X86N
D10, D11, D12, D13: PESD5V0S4UD; SOT95P275X110-6N
D14: SMA6J28A; DIOM5126X203N_SWP
J12: Molex_52207-1933_1x19-1MP_P1.00mm_Horizontal; CON-52207-1960; Manufacturer_PartNo 52207-1933
J13: S5B-ZR-SM4A-TF; CON-S5B-ZR-SM4A-TF
R33, R34, R35, R36, R37, R38, R39, R40, R42, R43, R45, R46, R47: 1k; RESC1608X50AN; Tolerance 1%
R41: 4.7k; RESC1608X50AN; Tolerance 1%
R44: 4.7k; RESC3216X60N; Tolerance 5%
R48: 62k; RESC1608X50AN; Tolerance 1%
R49: 10k; RESC1608X50AN; Tolerance 1%
RX1: TestPoint; TP-40R-NSA
TX1: TestPoint; TP-40R-NSA
U4: PIC18F43K22T-IPT; QFP80P1200X1200X120-44N

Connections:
+3.0VREF: U4.22 (RA3/AN3/Vref+/CAP2/QEA); also elsewhere on the board
+5V: C22.2, C23.2, C24.2, D13.1 (K1), J12.10, J13.2, R41.2, U4.7 (VDD), U4.28 (VDD); also elsewhere on the board
+VDC_PERM: D14.2 (K), J12.8; also elsewhere on the board
/BP: J12.9, R48.2; also elsewhere on the board
/CHARG_BAT1: U4.26 (AN6/P3B/RE1); also elsewhere on the board
/CHARG_BAT2: U4.24 (RA5/AN5/LVDIN); also elsewhere on the board
/DISCH_BAT1: U4.25 (AN5/CCP3/RE0); also elsewhere on the board
/DISCH_BAT2: U4.23 (RA4/AN4/CAP3/QEB); also elsewhere on the board
/FAN_EN: U4.11 (RB3/AN9); also elsewhere on the board
/IBAT_MEAS: U4.21 (RA2/AN2/Vref-/CAP1/INDX); also elsewhere on the board
/ID_BAT1: U4.14 (RB4/AN11); also elsewhere on the board
/ID_BAT2: U4.15 (RB5/AN13); also elsewhere on the board
/ID_BAT_READ: U4.44 (AN18/TX1/CK1/RC6); also elsewhere on the board
/Microcontroller block/BP_INFO: C25.2, R48.1, R49.2, U4.8 (RB0/AN12)
/Microcontroller block/MCLR: J13.1, R41.1, U4.18 (Vpp/~MCLR~/RE3)
/Microcontroller block/PGC: D10.6 (K4), J13.5, U4.16 (RB6/PGC)
/Microcontroller block/PGD: D10.4 (K3), J13.4, U4.17 (RB7/PGD)
/TEMP_BAT1: U4.10 (RB2/AN8); also elsewhere on the board
/TEMP_BAT2: U4.9 (RB1/AN10); also elsewhere on the board
/TEMP_MEAS: U4.1 (AN27/P1D/RX2/RC7); also elsewhere on the board
/VBAT1_MEAS: U4.19 (RA0/AN0); also elsewhere on the board
/VBAT2_MEAS: U4.20 (RA1/AN1); also elsewhere on the board
/V_CH: U4.2 (AN24/P2D/SD02/RD4); also elsewhere on the board
/V_DC_CHARGER: R44.2; also elsewhere on the board
/V_EN: U4.3 (AN25/P1B/RD5); also elsewhere on the board
GND: C22.1, C23.1, C24.1, D10.2 (A), D10.5 (A), D11.2 (A), D11.5 (A), D12.2 (A), D12.5 (A), D13.2 (A), D13.5 (A), D14.1 (A), J12.18, J12.19, J13.3, U4.6 (VSS), U4.29 (VSS); also elsewhere on the board
GNDA: C25.1, R49.1; also elsewhere on the board
unnamed: D10.1 (K1), J12.2, R46.1
unnamed: D10.3 (K2), J12.1, R47.1
unnamed: D11.1 (K1), J12.6, R40.1
unnamed: D11.3 (K2), J12.5, R42.1
unnamed: D11.4 (K3), J12.4, R43.1
unnamed: D11.6 (K4), J12.3, R45.1
unnamed: D12.1 (K1), J12.14, R36.1
unnamed: D12.3 (K2), J12.13, R39.1
unnamed: D12.4 (K3), J12.12, R37.1
unnamed: D12.6 (K4), J12.11, R38.1
unnamed: D13.3 (K2), J12.17, R33.1
unnamed: D13.4 (K3), J12.16, R34.1
unnamed: D13.6 (K4), J12.15, R35.1
unnamed: J12.7, R44.1
unnamed: R33.2, U4.43 (AN17/SDO1/RC5)
unnamed: R34.2, U4.42 (AN16/SDI1/SDA1/RC4)
unnamed: R35.2, U4.41 (AN23/P2C/~SS2~/RD3)
unnamed: R36.2, U4.40 (AN22/P2B/RD2)
unnamed: R37.2, U4.38 (AN20/SCK2/SCL2/RD0)
unnamed: R38.2, U4.37 (AN15/SCK1/SCL1/RC3)
unnamed: R39.2, U4.39 (AN21/CCP4/SDI2/RD1)
unnamed: R40.2, U4.36 (AN14/CCP1/T5CKI/RC2)
unnamed: R42.2, U4.35 (SOSCII/CCP2/RC1)
unnamed: R43.2, U4.32 (SOSCO/T1CKI/RC0)
unnamed: R45.2, U4.31 (RA6/OSC2/CLKO)
unnamed: R46.2, U4.30 (RA7/OSC1/CLKI)
unnamed: R47.2, U4.27 (AN7/CCP5/RE2)
unnamed: RX1.1, U4.5 (AN27/P1D/RX2/RD7)
unnamed: TX1.1, U4.4 (AN26/P1C/TX2/RD6)

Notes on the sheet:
Note: Place J13 conn in the upper Bottom side
Note: J12 conn - SMD component, place on Bottom left side
ICSP Prog

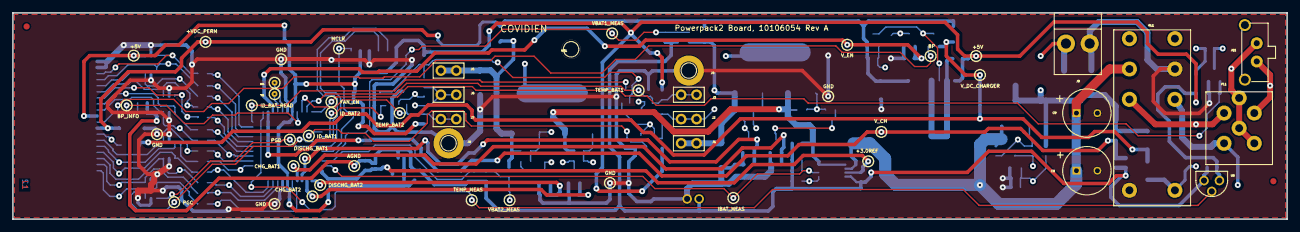
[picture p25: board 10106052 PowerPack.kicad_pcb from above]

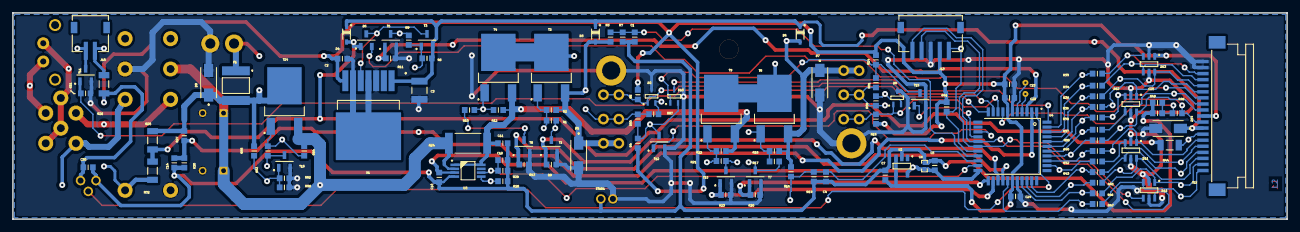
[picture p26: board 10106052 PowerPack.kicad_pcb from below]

Board: 2 copper layers, 210.0 x 34.0 mm, 133 parts (113 on the bottom side), 92 nets.

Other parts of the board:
FID1, FID2: FIDUCIAL; FIDUCIAL_1
MT1: MTHOLE1; MTHOLE1_1

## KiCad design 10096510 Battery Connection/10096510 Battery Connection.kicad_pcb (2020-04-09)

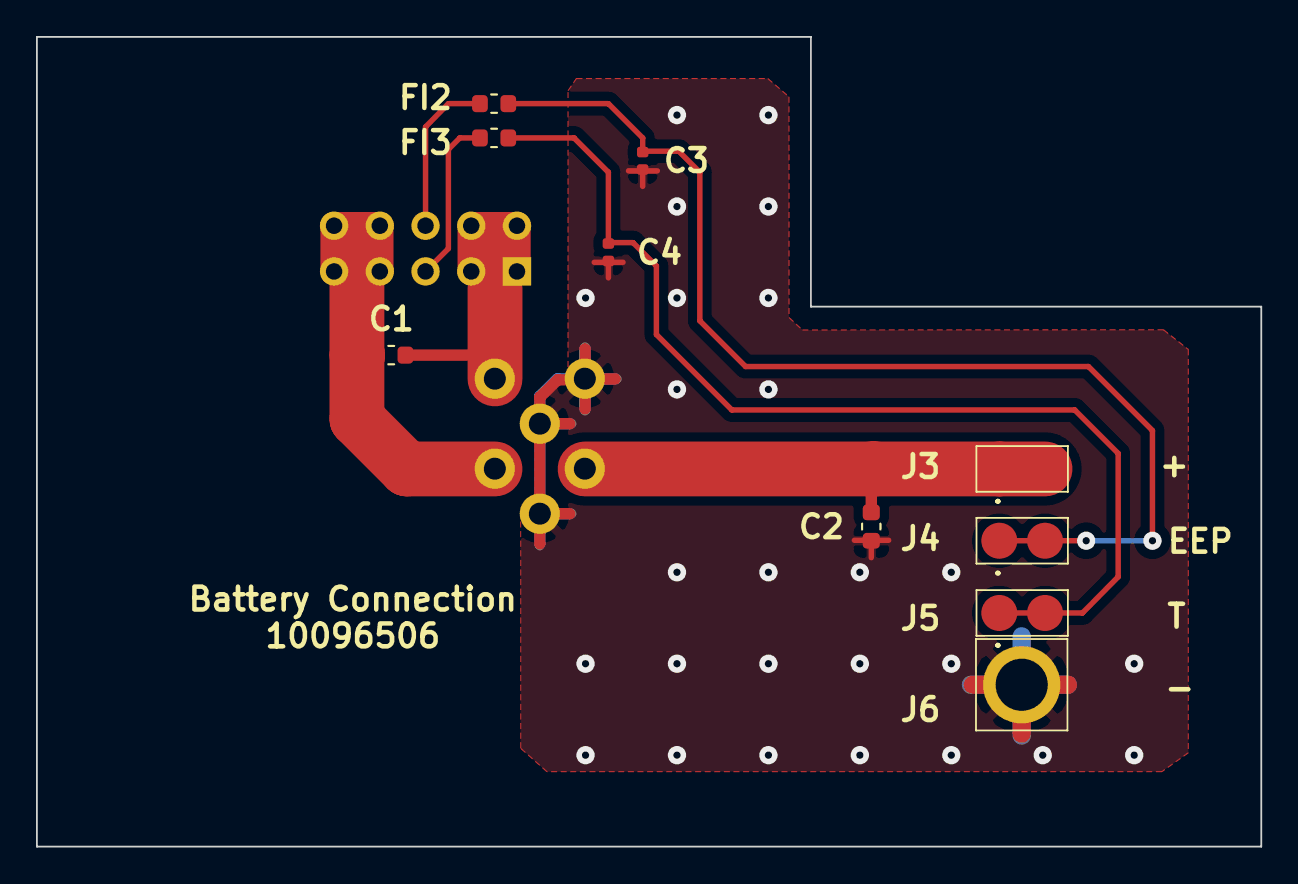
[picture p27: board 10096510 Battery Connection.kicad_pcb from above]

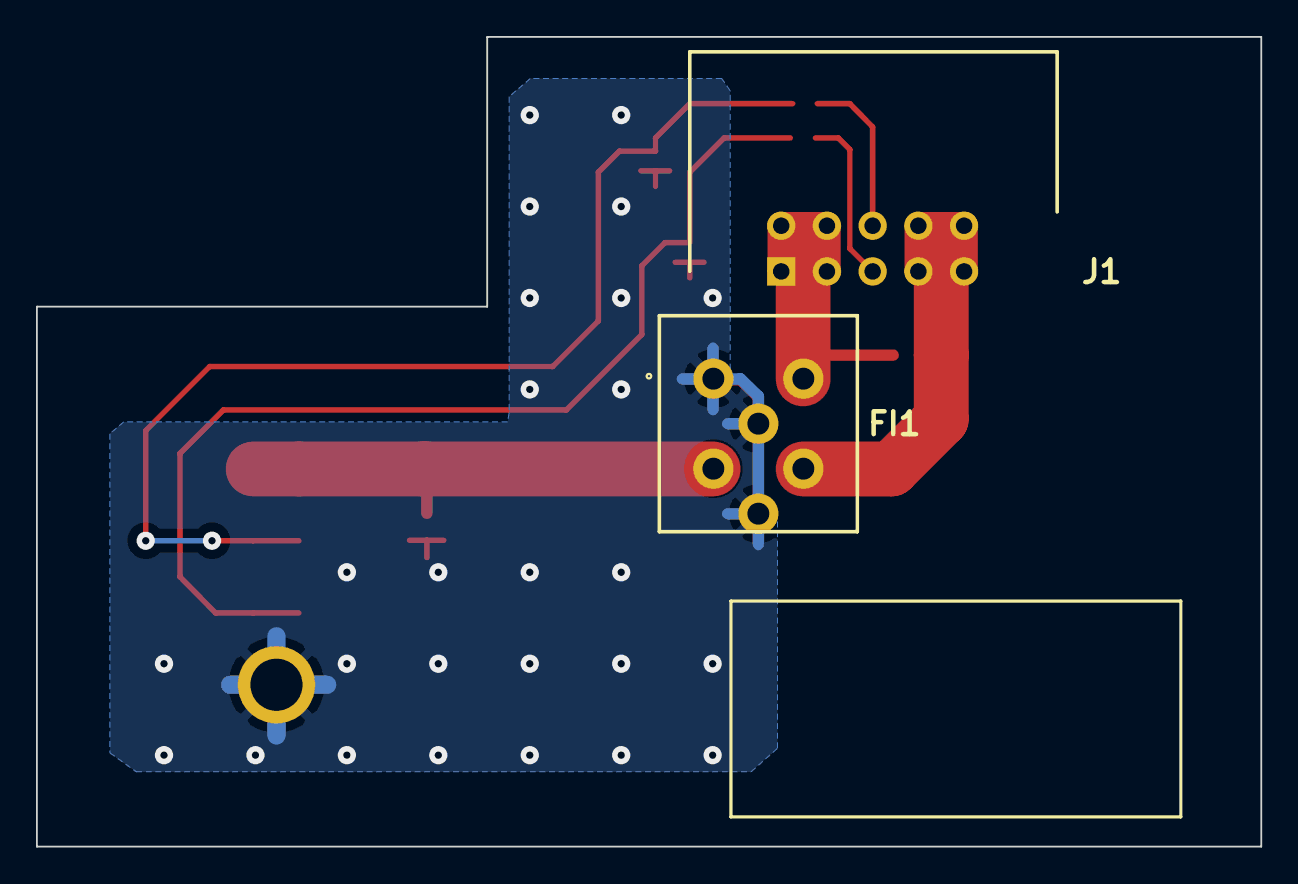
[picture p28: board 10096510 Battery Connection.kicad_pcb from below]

Board: 2 copper layers, 68.0 x 45.0 mm, 12 parts (2 on the bottom side), 8 nets.

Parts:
C1, C2: 10nF; C_0603_1608Metric
C3, C4: 0402_47pF_C0402C470J5GAC; C_0402_1005Metric
FI1: BNX002-11; BNX002-011
FI2, FI3: 74279266; L_0603_1608Metric
J1: 09185107323; SHDRRA10W64P254_2X5_2050X890X930P
J3, J4, J5: 811-S1-002-30-014101; CONN_811S100230014101
J6: GKS-913-0024; CONN_GKS-913-Z

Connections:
/+: C2.2, FI1.2, J3.1, J3.2
/BAT_EEPROM: C3.1, FI2.1, J4.1, J4.2
/T: C4.1, FI3.2, J5.1, J5.2
Earth: C1.1, FI1.3, J1.1, J1.2, J1.3, J1.4
GND: C2.1, C3.2, C4.2, FI1.4, FI1.5, FI1.6, J6.1
unnamed: FI2.2, J1.6
unnamed: FI3.1, J1.5
VDD: C1.2, FI1.1, J1.7, J1.8, J1.9, J1.10

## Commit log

2020-04-01 Initial commit of empty projects and license
    [10005011 Power Management.kicad_pcb, 10005011 Power Management.sch, 10096315 Blower Driver.kicad_pcb, 10096315 Blower Driver.sch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]
2020-04-02 Update Memory page of CPU
    [CPU_RB0505.sch, memory.sch]
2020-04-03 Upload New File
    [10096510_Battery_Connection.sch]
2020-04-03 Adding CPU
    [CPU_RB0505.sch, cpu.sch, memory.sch]
2020-04-03 hierarchical blocks on top level, +5V and fan block
    [10106052 PowerPack.sch, 3V_reference_voltage.sch, 5V_power_supply.sch, ambient_temperature_measurement.sch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]
2020-04-03 Update CPU sheet
    [cpu.sch, memory.sch]
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2020-04-04 Initial Microntroller Work
    Created the PIC symbol
    Started the initial schematic page
    [3V_reference_voltage.sch, 5V_power_supply.sch, ambient_temperature_measurement.sch, microcontroller_block.sch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]
2020-04-04 Initial MCU page
    [microcontroller_block.sch]
2020-04-04 Updating CPU sheet
    [cpu.sch]
2020-04-04 Cleanup extra pro files and rescue library
    [10106052 PowerPack.sch, 3V_reference_voltage.sch, 5V_power_supply.sch, ambient_temperature_measurement.sch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]
2020-04-04 start to create switching block
    [10106052 PowerPack.sch, 3V_reference_voltage.sch, 5V_power_supply.sch, ambient_temperature_measurement.sch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]
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2020-04-04 Replace 10096510 Battery Connection.kicad_pcb
    [10096510 Battery Connection.kicad_pcb]
2020-04-04 Replace 10096510 Battery Connection.sch
    [10096510 Battery Connection.sch]
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2020-04-04 schematic done2
    [switching_block.sch]
2020-04-04 +3V ref schematic block added
    [10106052 PowerPack.sch, 3V_reference_voltage.sch]
2020-04-04 temperature measurement schematic added
    [10106052 PowerPack.sch, ambient_temperature_measurement.sch]
2020-04-04 micro block schematic done
    [5V_power_supply.sch, microcontroller_block.sch]
2020-04-05 Adding ICs, resistors, diodes, mosfets to blower library
    [10096315 Blower Driver.sch]
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2020-04-05 Starting power supply schematic
    [10096315 Blower Driver.sch]
2020-04-05 Library Field Changes
    [5V_power_supply.sch, ambient_temperature_measurement.sch, microcontroller_block.sch]
2020-04-05 Placed majority of components, ferrites, filters, connectors left
    [10096315 Blower Driver.sch]
2020-04-05 Placing connectors
    [10096315 Blower Driver.sch]
2020-04-05 reorganize blocks
    [utils.sch]
2020-04-05 PowerPack schematic toplevel done
    [10106052 PowerPack.sch, 3V_reference_voltage.sch, 5V_power_supply.sch, ambient_temperature_measurement.sch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]
2020-04-05 Added ICSP Prog label
    [10106052 PowerPack.sch, microcontroller_block.sch, utils.sch]
2020-04-05 Powerpack dev
    [10106052 PowerPack.sch, 3V_reference_voltage.sch, 5V_power_supply.sch, ambient_temperature_measurement.sch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]
2020-04-05 Import drawing as Cmts.User layer
    [10106052 PowerPack.kicad_pcb, 10106052 PowerPack.sch]
2020-04-05 Finished first version of blower driver schematic
    [10096315 Blower Driver.sch]
2020-04-05 Updated schematic with main bus capacitance
    [10096315 Blower Driver.sch]
2020-04-05 Added net tie
    [10096315 Blower Driver.sch]
2020-04-05 PCB Added and Schematic Footprints Added
    [10106052 PowerPack.kicad_pcb, switching_block.sch, utils.sch]
2020-04-05 Continuing CPU work
    [cpu.sch, memory.sch]
2020-04-05 Adding first pass at Buzzer Board schematic
    [GR106768 Buzzer.sch, GR106768_buzzer_charger.sch]
2020-04-05 Changed global nets to hierarchical
    [GR106768 Buzzer.sch, GR106768_buzzer_charger.sch]
2020-04-05 Finalizing reference designators per issue #12. Added missing C24-C26 (100 nF decoupling caps for +24V). Added no-connect symbols. Added some previously missing ground ties on a couple ICs. Added V-R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
    [10096315 Blower Driver.sch]
2020-04-05 Updated battery connection schematics. Put all components in board-specific library. Updated symbols to include datasheets, manufacturers, manufacturer part numbers, etc. Updated connector symbols to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
    [10096510 Battery Connection.sch]
2020-04-05 ERC fixes: replaced hierarchical pins with local net labels
    [10096315 Blower Driver.sch]
2020-04-06 ERC fixes (this should put ERC at 0 warnings/errors): Fixed library parts with duplicate pin numbers. Fixed some library parts having pins with inappropriate electrical types (e.g. linear regulator).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
    [10096315 Blower Driver.sch]
2020-04-06 Created TestPoint symbol in Blower_Driver_Components library and added an instance to schematic at ref PT1
    [10096315 Blower Driver.sch]
2020-04-06 Added parameters to components
    [microcontroller_block.sch, switching_block.sch, utils.sch]
2020-04-06 Added missed hierarchial labels
    [GR106768_buzzer_charger.sch]
2020-04-06 Fixed U4 pins (KiCad part is different)
    [GR106768 Buzzer.sch]
2020-04-06 Merged Buzzer libraries into master library
    [GR106768 Buzzer.sch, GR106768_buzzer_charger.sch]
2020-04-06 added 3V reference block in high level. Update 3V reference schematics
    [10005011 3V Reference.sch, 10005011 Power Management.sch]
2020-04-06 Fixed missing pin 6 on BNX002-11 symbol. Updated footprint to match existing layout pin configuration for BNX002-11. Aligned components to placement on current design. Started routing. Layout still w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
    [10096510 Battery Connection.kicad_pcb]
2020-04-06 Created Project Footprint Library
    [switching_block.sch, utils.sch]
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2020-04-06 Footprints relinked
    [10106052 PowerPack.kicad_pcb, 10106052 PowerPack.sch, microcontroller_block.sch, switching_block.sch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]
2020-04-07 Added 3D Models, corrected orientation of parts on schematic, added TX/RX TP
    [026614020.stp, 4131.stp, 4152 v1.step, 4152.stp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]
2020-04-07 Corrected BNX00201 and SUD50P06-15L-E3 Symbols to Match Footprint
    [microcontroller_block.sch, switching_block.sch]
2020-04-07 Merge branch 'master' of https://gitlab.com/openventilator/openventilator into batteryconnector-dev
    WIP.
    Updated hole and pad sizes to match imported design files for connectors & filter and fixed filter pinout.
    Added silk for label.
    [10096510 Battery Connection.kicad_pcb, 10096510 Battery Connection.sch]
2020-04-07 WIP. Merged the layout conversion info from George. Updated library footprint pads for filter and through-hole connectors per the layout conversion info. Added gnd planes and sitching vias. Added ass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
    [10096510 Battery Connection.kicad_pcb]
2020-04-07 WIP - Working to address library syncing.
    [10096510 Battery Connection.kicad_pcb, 10096510 Battery Connection.sch]
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2020-04-07 WIP to address library sync issues.
    [10096510 Battery Connection.sch]
2020-04-07 Updating Buzzer and start of board
    [GR106768 Buzzer.kicad_pcb, GR106768 Buzzer.sch, GR106768_buzzer_charger.sch]
2020-04-07 Schematic Synched to PCB
    [10106052 PowerPack.kicad_pcb, 10106054A00_Original_DesignRules.XLS]
2020-04-08 Initial Imported PCB & Paul's Work
    [10005011 Power Management Updated Bill of Materials.xls, 10005011 Power Management.kicad_pcb]
2020-04-08 Oops - adding stuff that should have been added by previous commit
    [10096315 Blower Driver.kicad_pcb, 10096315 Blower Driver.sch]
2020-04-08 Updating Molex MPNs for J3 and J6 to those recommended as replacements to the EOL Medtronic parts
    [10096315 Blower Driver.sch]
2020-04-08 Manually reverting my previous edits because I'm not sure how to do it automatically lol
    [10096315 Blower Driver.sch]
2020-04-08 Adding datasheet links for J6/J3 back in
    [10096315 Blower Driver.sch]
2020-04-08 added power flags to library and PIC to schematic
    [10005011 3V Reference.sch, 10005011 Micro Controller.sch, 10005011 Power Management.sch]
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2020-04-09 Added mounting holes, fiducials; fixed some footprint library weirdness
    [10096315 Blower Driver.kicad_pcb, 10096315 Blower Driver.sch]
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2020-04-09 Fixed drill size on stitching vias. WIP - cleaning copper pours.
    [10096510 Battery Connection.kicad_pcb]
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2020-04-09 Possibly goofed up the conflict resolution last time - I think this should fix it
    [10096315 Blower Driver.kicad_pcb]
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2020-04-09 Updated with George's exported PCB. Fixed pin-pad associations. Still need net-tie placement and to fix one weird issue with pad 2 of J4 not being recognized
    [10096315 Blower Driver.kicad_pcb, 10096315 Blower Driver.sch]
2020-04-10 Fixed footprint/symbol pin orientation, assigned missing nets to all tracks and pours
    [10096315 Blower Driver.kicad_pcb, 10096315 Blower Driver.sch]
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2020-04-10 Added net-tie, fixed pin assignment for SOD323
    [10096315 Blower Driver.kicad_pcb, 10096315 Blower Driver.sch]
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2020-04-12 Corrected merge errors on sheet 5
    [10125623A00_5.sch]
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2020-04-13 Sheet 3 global label shape fixed
    [10125623A00_3.sch]
2020-04-13 Global Labels with '/' character changed to '\'
    Kicad doesn't allow the former
    [10125623A00_1.sch, 10125623A00_2.sch, 10125623A00_3.sch, 10125623A00_4.sch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]
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2020-04-13 Sheet2: Fixed to grid - busses and labels need review
    [10125623A00_2.sch]
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2020-04-14 Fixed the grid for sheet 1.
    [10125623A00_1.sch]
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
